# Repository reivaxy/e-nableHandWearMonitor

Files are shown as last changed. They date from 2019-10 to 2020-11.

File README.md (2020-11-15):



# e-nableHandWearMonitor

This device is intended to track the time spans during which an E-nable device is worn by its owner.

## How does it work?

It uses a sensor to detect that the device is worn. Two types of sensors are supported: either a pair of metallic contacts that should be in contact with the skin when the device is worn, or an infrared sensor, that does not need any contact with the skin, which avoids the risk of allergies.

The device has two modes: "recording" and "charging".

In "recording mode" which is as long as the battery lasts, and not plugged into an usb charger, the Esp8266 wakes up at a period that can be set and saved in permanent memory (default is every 5 seconds), checks the presence sensor, and compares its state to the previous time it was checked.

If there is a difference, and for the third time in a row, it records the date and time in a file, in the Esp flash memory, saves the new state, and goes back to deep sleep until it automatically wakes up again.

The "third time in a row" condition insures to not record transient changes that may be due to handling the device while strapping it on, or whatever.

If there is no difference, it just goes back to deep sleep without recording anything.

This allows to save battery life (from 1 to 3 weeks depending on model).

In "charging mode", which is when an usb charger is plugged in, it keeps doing the check but every 2 seconds, won't record any changes, and won't sleep.

Instead it opens up a wifi access point, and  the blue led blinks every 2 seconds to indicate the wifi is activated. When the device has not been set up (or as been reset to factory defaults), the default wifi network SSID is "HandMonitor", and password is the same.

**IMPORTANT: The password should be modified while setting up the device**.

By connecting your phone to this network, you can access the module pages at http://192.168.4.1.

If some settings were already saved at least once, the home page will be displayed.

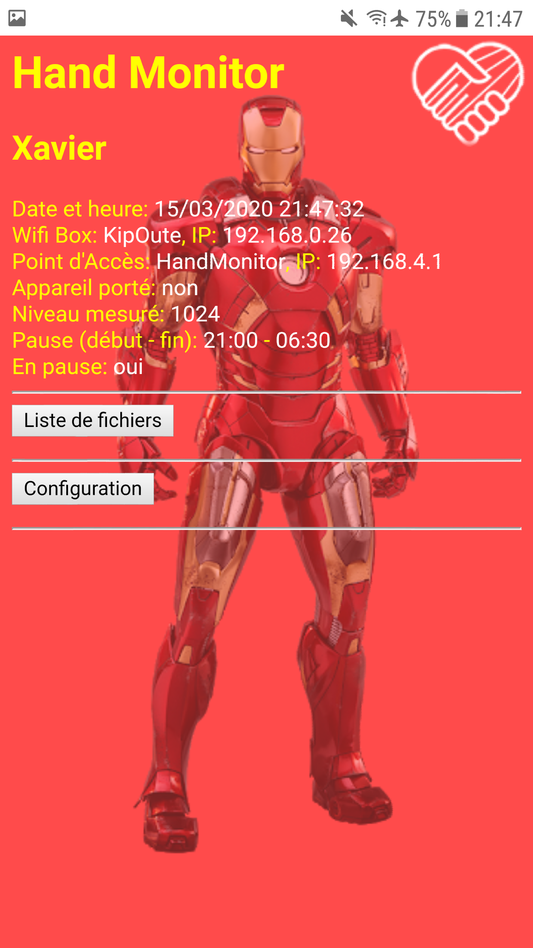
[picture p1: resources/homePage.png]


If the device has never been set up, the settings page will be displayed. 

## The settings page

Here is what the setup settings looks like with a custom skin (more on that later):

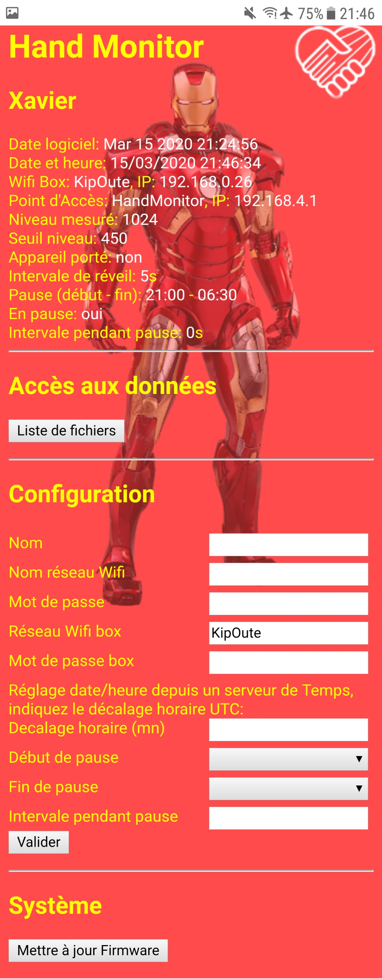
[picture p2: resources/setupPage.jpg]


You should provide a name for the device, for instance its owner first name.

You can change the default ssid/pwd **(please change at least the password)** for the access point wifi network, and, optionally, provide your home wifi ssid and pwd. These are stored locally in the device memory, and never sent anywhere.

Providing your home wifi connection information will allow to automatically setup the date and time in the device, and will allow you to download the data files listing each period the E-nable hand was worn to your computer, and upload file to customize the apparence.

If you don't provide your home wifi connection information you will be able to setup the time manually (work in progress), and download the data files to your computer or phone.

The setup page also displays an "Update firmware" button. When you click on it the device will toggle to OTA (Over the Air) mode, and wait for a new firmware to be uploaded. The blue led will blink twice per second in this mode.

You can then use an android app like "ESP8266 Loader" to upload the new binary from your phone connected to its wifi network, using the device default IP 192.168.4.1

If you provided your home wifi connection information, the update can also be made using the device IP on this network.

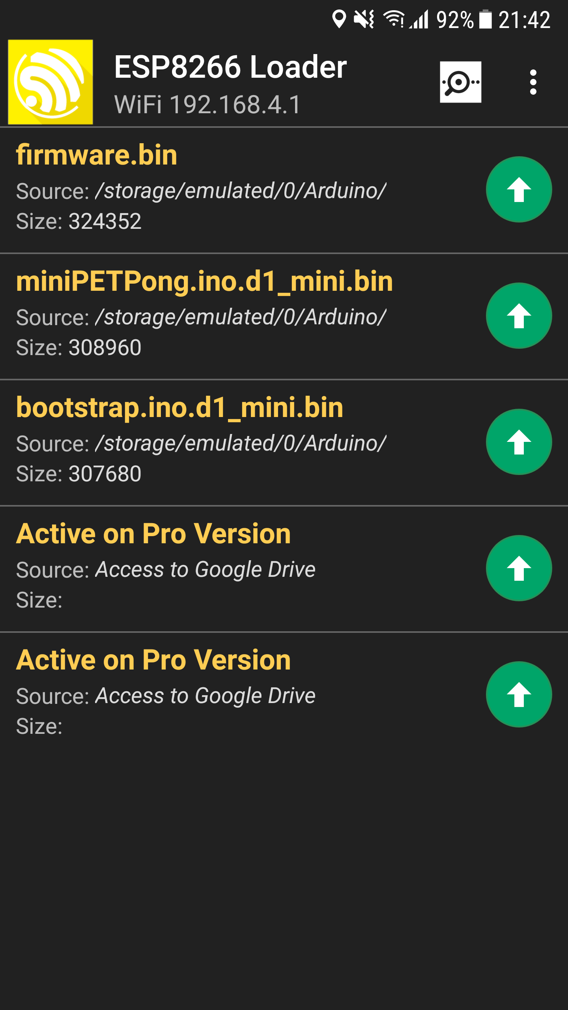
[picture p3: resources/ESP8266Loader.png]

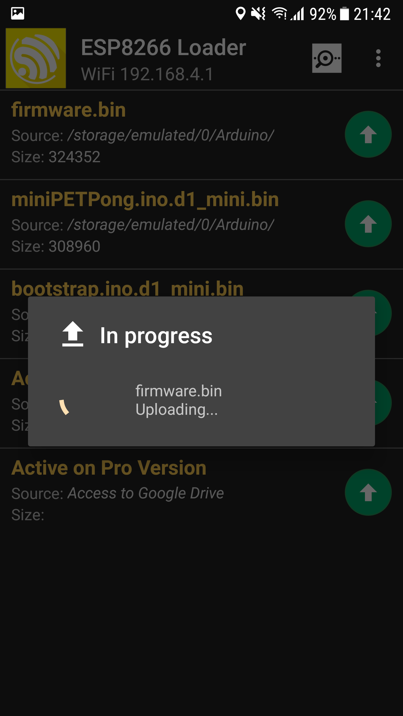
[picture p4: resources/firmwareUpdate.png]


In case a bug breaks the OTA feature in a firmware build, it can still be updated by opening the lid and using the 5 pad solderless connector with a special device to upload a fix through USB connection.

Whatever the upgrade method chosen (OTA or USB), the blue led on the esp will flash frantically while the firmware is uploading.

After the upload is done (and verified) the esp will reboot, updated, and reopen the wifi networks depending on the settings provided.

## Data

The "File list" button will display a page listing all the files in the esp memory. One new file is created each month.

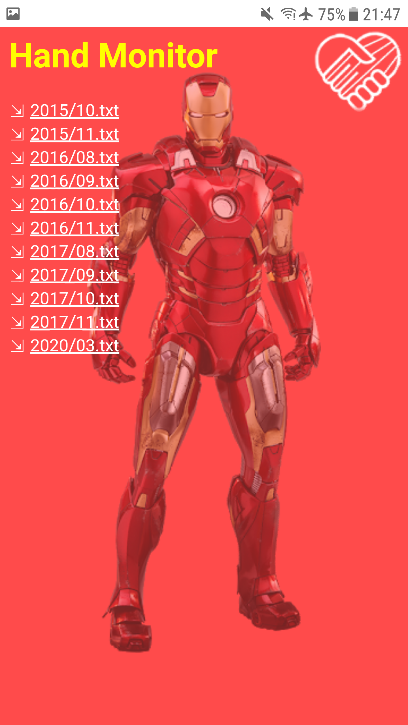
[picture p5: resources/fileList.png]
<kbd></kbd>

You can click on a file name to view its content, or on the arrow in front of it to download it.

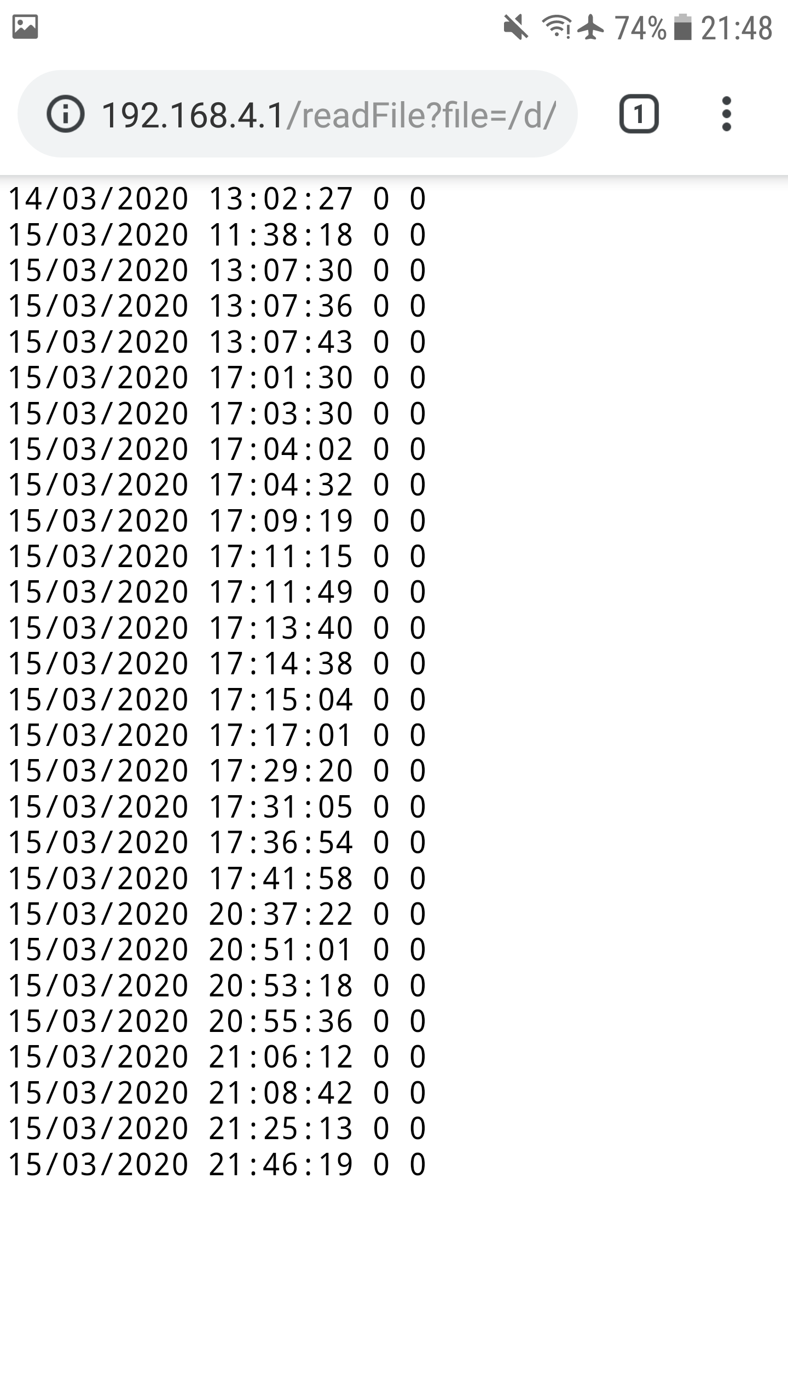
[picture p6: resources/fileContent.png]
<kbd></kbd>

I had no issue recording 15695 lines, in a 223K file (at the time, only the day was saved instead of the full date). 

Each entry is composed of the date, then the hour, minute, second, then the state: 0 means device not worn, 1 means device worn. The actual level of the sensor is then added to the line, to help troubleshoot, if necessary.

A graphical representation of this data can be obtained by dropping one such file [on this webpage](https://reivaxy.github.io/handMonitorDataViz/)
                                                     Data is not uploaded anywhere, and this visualisation tool can be installed locally on any computer without needing a webserver


## "Admin" page

It's a page where some more configuration data as well as "dangerous" features are available: reset the full device (configuration and data files), erase all data files, create test data files...

On this page you can update the wake up period as well as the sensor level threshold that is used to decide if the device is being worn (by detecting skin proximity) or not.

There is also some information on the SPIFFS memory usage, and more will be added if needed.

The "upload file" feature allows you to change the look of the pages if you upload a "custom.css" file. You can also upload images referenced in the css file. Check out the data/w directory for an example featuring an ironman skin.

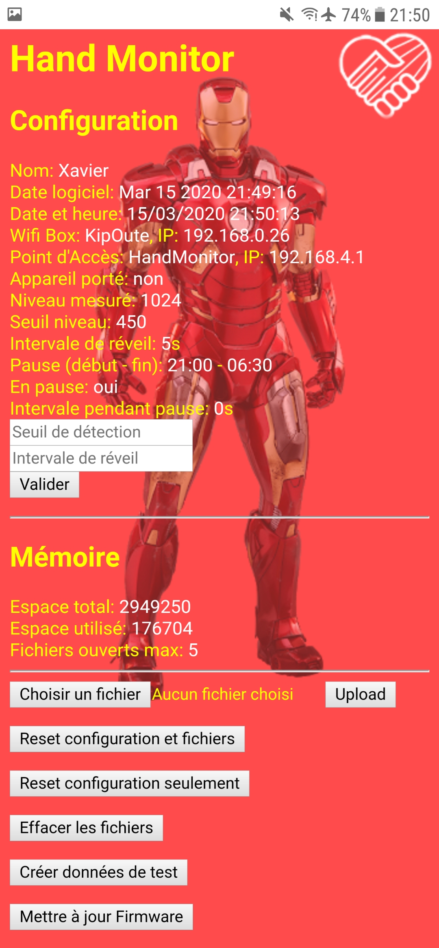
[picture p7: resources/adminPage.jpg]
<kbd></kbd>

## The 1000 mAh version

The prototype shown was built using a 1000mAh battery, which provides an autonomy of more than two weeks.

It is not using the definitive PCB, some wires will be removed, some layout improved to ease assembly.

Here are pictures of this device in its 3D printed case with a slide-in lid:

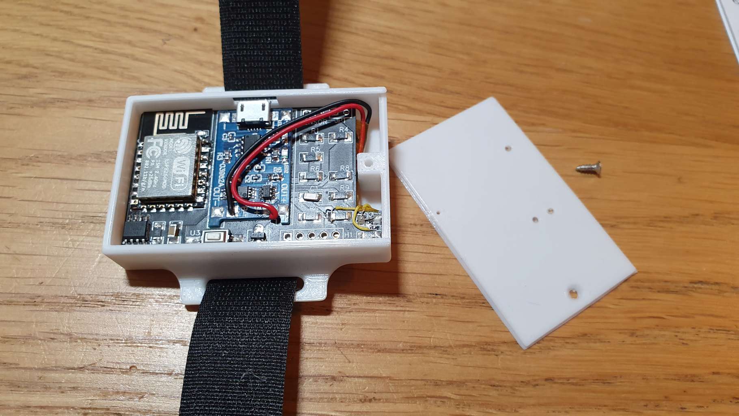
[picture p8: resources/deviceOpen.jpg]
<kbd></kbd>

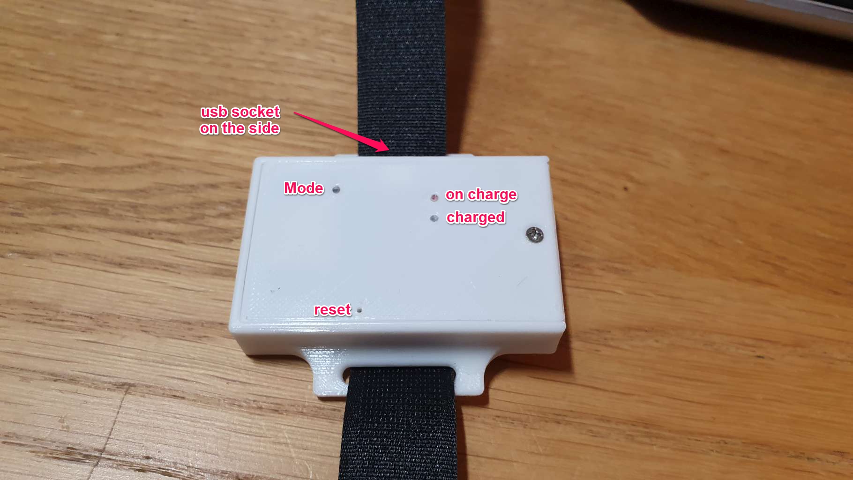
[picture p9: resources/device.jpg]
<kbd></kbd>

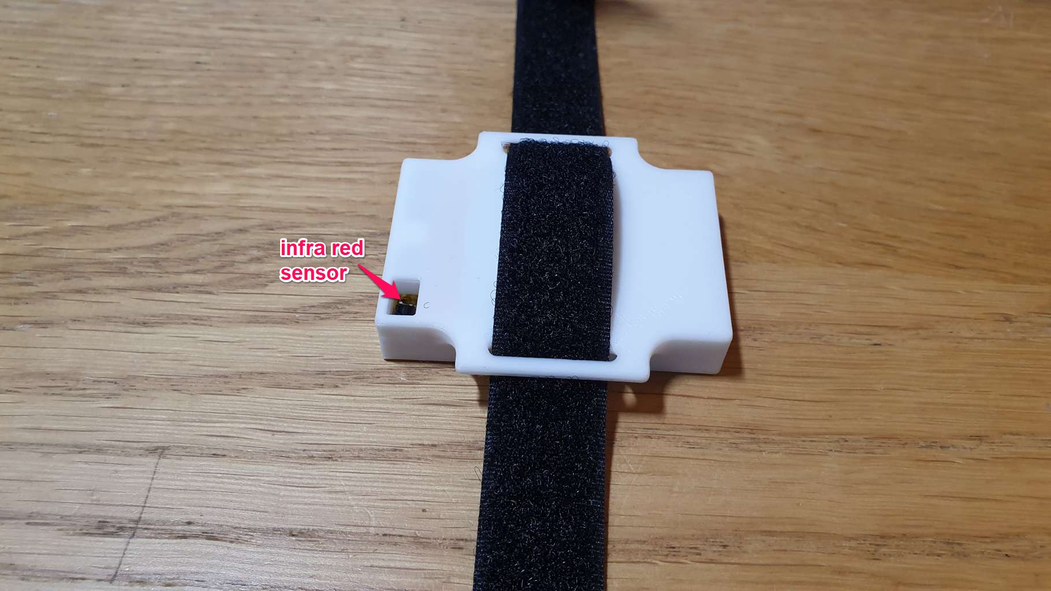
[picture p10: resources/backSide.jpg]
<kbd></kbd>

Solderless connections available on the PCB allow to monitor the serial port for debug messages, as well as flash a new release of the firmware in case OTA feature is broken.

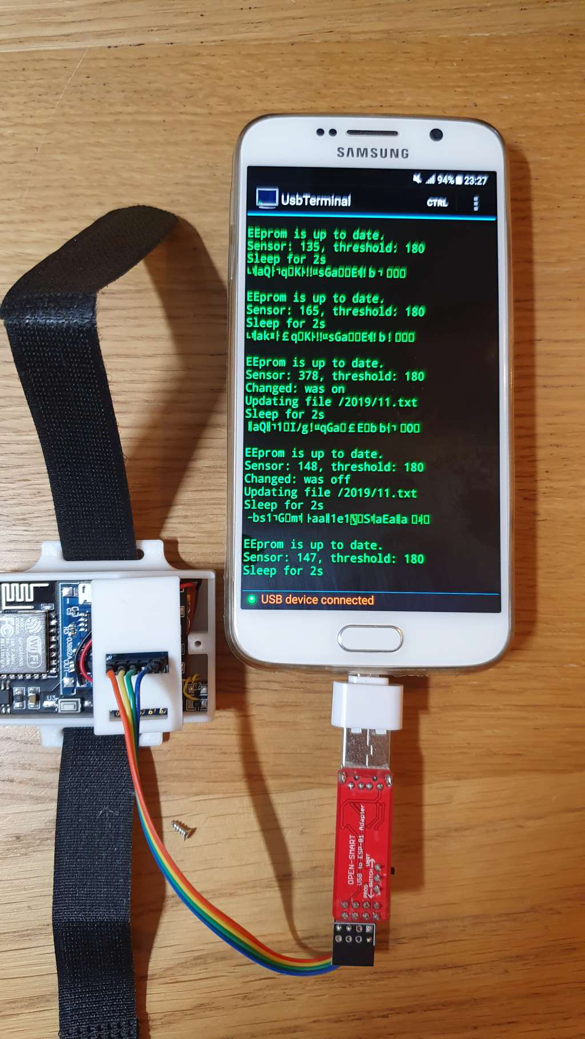
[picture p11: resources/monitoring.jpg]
<kbd></kbd>

Using a custom tool that clips in the lid rails:

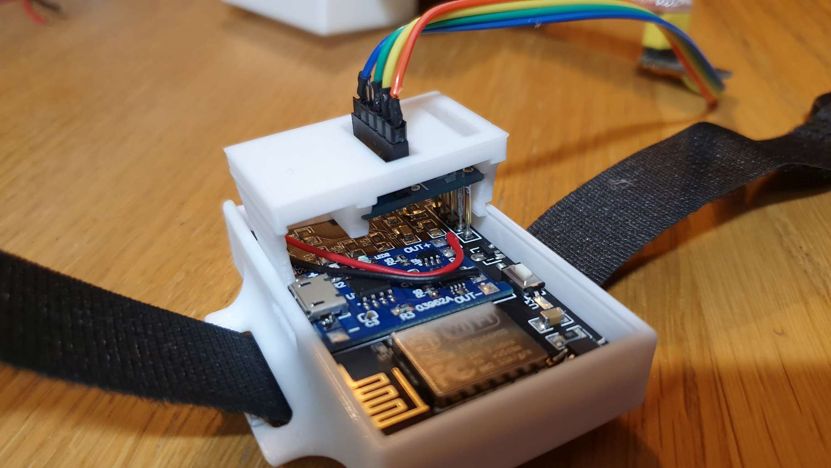
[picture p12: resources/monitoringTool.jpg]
<kbd></kbd>

The PCB is very thin to minimize weight and volume. This prototype PCB has a faulty IR sensor package layout and incorrect battery connection to charger, fixed for next version.

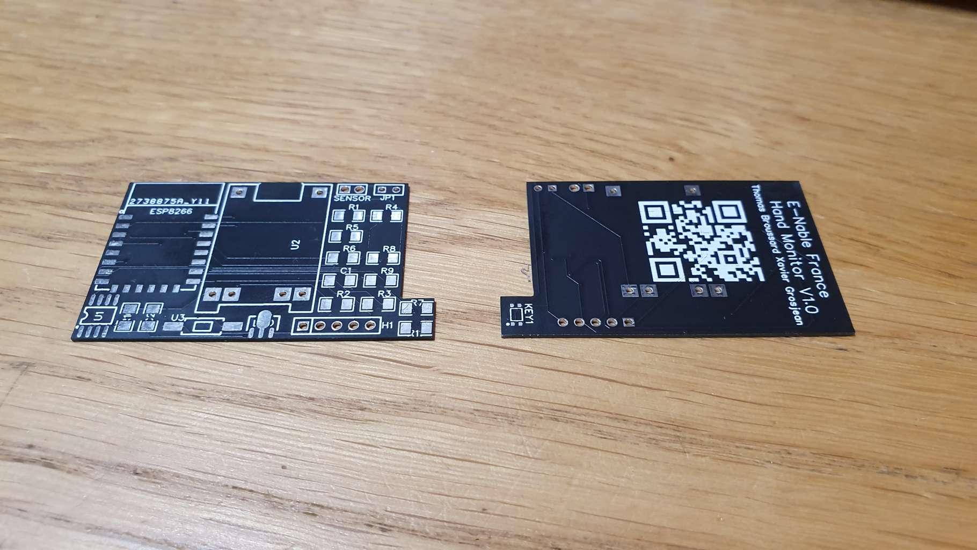
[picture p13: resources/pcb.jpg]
<kbd></kbd>

 ## The 300 mAh version

 The model above is a bit too big and too heavy for young kids, so I built another one, much smaller, using a 300mAh battery, which still gives it a little over one week of autonomy.

 This is the first prototype.

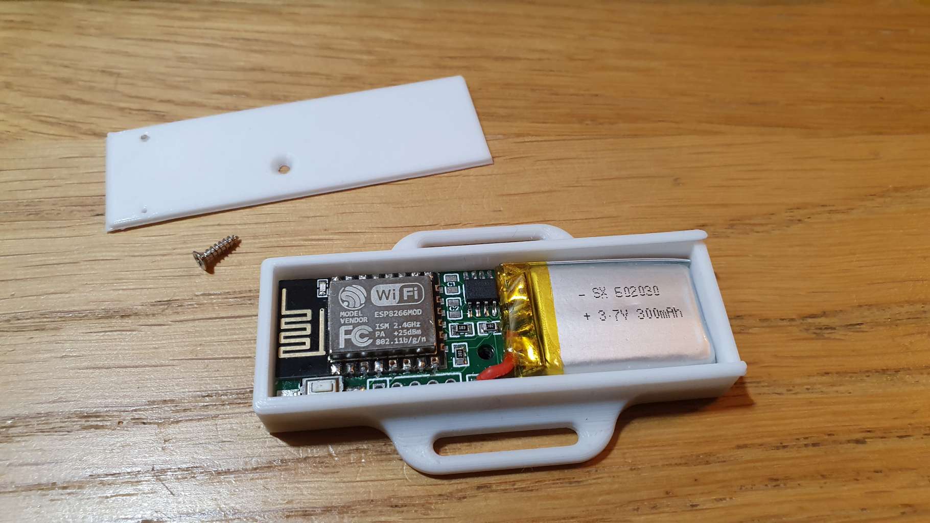
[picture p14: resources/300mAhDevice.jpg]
<kbd></kbd>

Since its shape is a bit long, it is not convenient for a small hand (printed at 100% scale), which is why I designed this third layout:

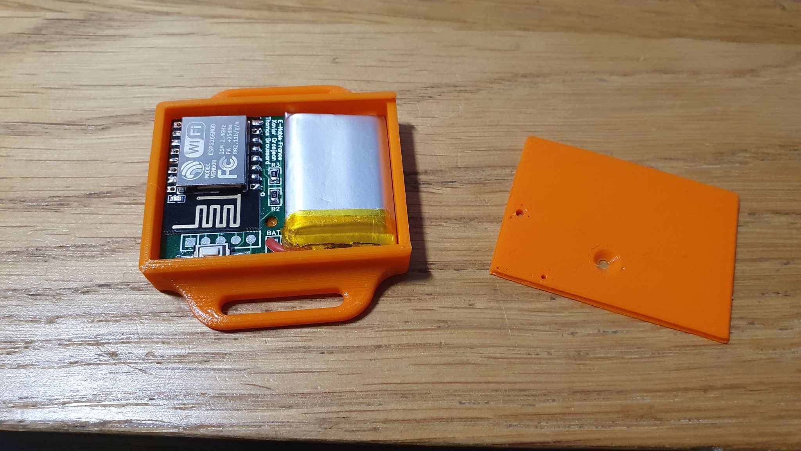
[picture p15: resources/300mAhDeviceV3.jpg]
<kbd></kbd>

All PCB's are (or will be made) available in the repository, as well as 3D designs to 3D-print the cases and the clip-on device to access serial connection for debuging or flashing firmware.

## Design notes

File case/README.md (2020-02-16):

# 3D files for case, lid and clip-on connector

Here are the source files to 3D print the cases for the handmonitor.

The dimensions need to be accurate for the PCB and battery to fit tightly, and the PCB should be 0.8mm thick.

The V1, aka "1000mAh", version is available in 1 layout.

The 300mAh version is available in 2 layouts:

- V2: long case

- V3: squarrish case  NOT READY FOR REAL PCB YET, just a POC

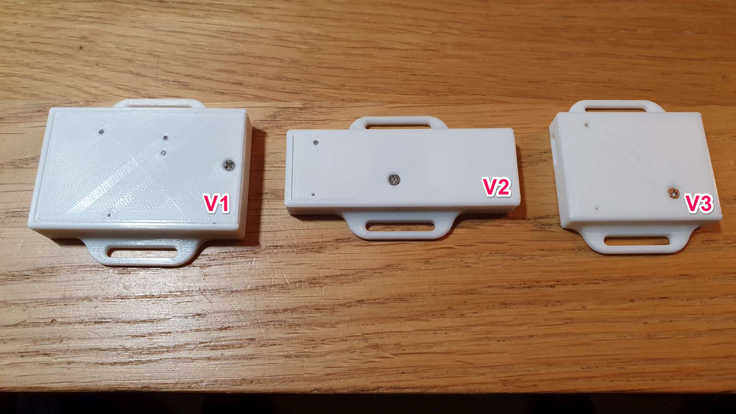
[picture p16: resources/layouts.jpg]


The 3 small holes for the mode and charging LEDs are intended to be filled with a small bit of  ⌀1mm plastic optical fiber.

# Black well for better results
Ideally, the IR sensor well should be printed in black, to improve sensor levels differenciation between "worn" and "not worn" states.

Using the same elctronic device in the two cases below, the level on the sensor when the device was not worn was twice as high with the black well than with the white well.

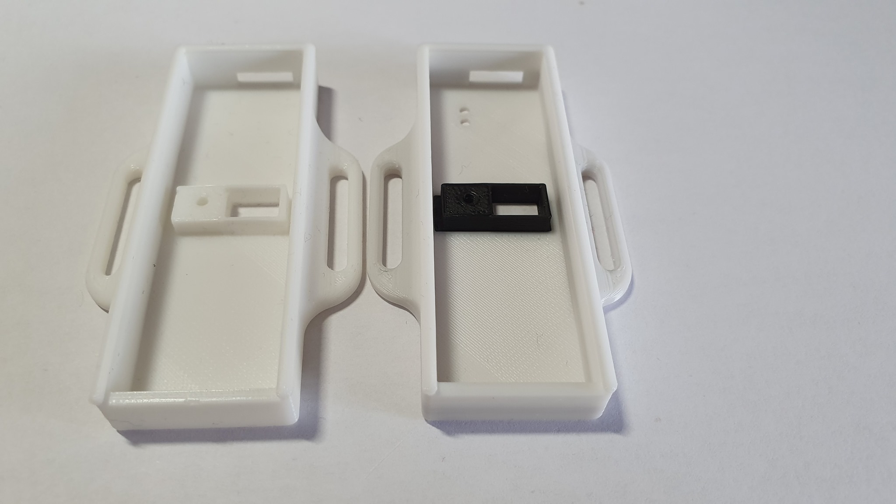
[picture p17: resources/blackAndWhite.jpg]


When printing a black well is not possible then its inside walls should be painted with black acrylic paint, for instance.

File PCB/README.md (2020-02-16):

# Fabrication files.

If you are going to use the provided STLs to 3D print the case, make sure to order a 0.8mm pcb

Several different PCBs were actually made for each version (1000mAh and 300mAh), but the schematic is identical for each.



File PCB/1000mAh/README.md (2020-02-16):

# Fabrication files for 1000mAh version PCB

If you are going to use the provided STLs to 3D print the case, make sure to order a 0.8mm pcb

V1.0 is buggy due to incorrect IR detector package. It is still in this repo since 5 PCBs were made

V1.1 fixes that, along with some layout change to ease component soldering

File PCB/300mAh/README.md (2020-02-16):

# Fabrication files for 300mAh version PCB

If you are going to use the provided STLs to 3D print the case, make sure to order a 0.8mm pcb

## V2 is the long version.

V2.0 is not optimal for ESP led position, that might be hidden by scratch band when using provided case STL. 

V2.1 fixes that by rotating ESP

## V3 is the squarrish version.
No issue reported so far.

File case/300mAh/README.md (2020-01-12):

If possible, the well (hole for the IR sensor) should be printed in black in order to less reflect the IR light to the sensor.

It helps setting the threshold to a value that ensures no detection error.

The hook should be printed in ABS for more elasticity. It's tight, and PLA breaks too easily.

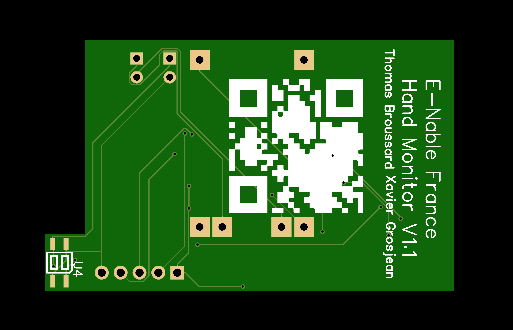
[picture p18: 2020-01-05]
PCB/1000mAh/V1.1_BOTTOM.png

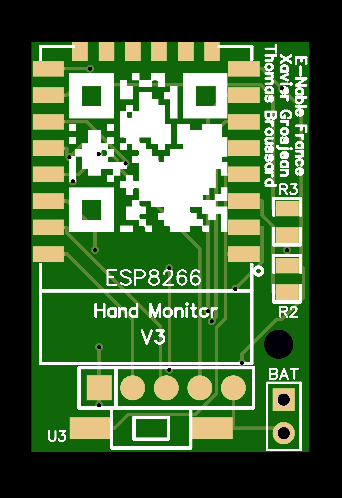
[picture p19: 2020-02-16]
PCB/300mAh/V3/V3.0_TOP.png

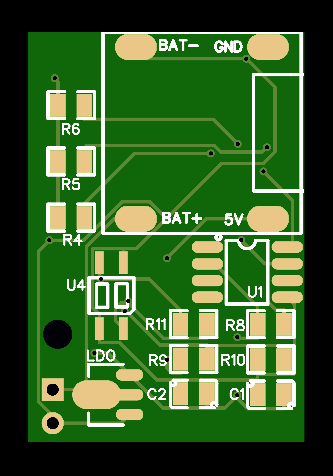
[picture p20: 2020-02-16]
PCB/300mAh/V3/V3.0_BOTTOM.png

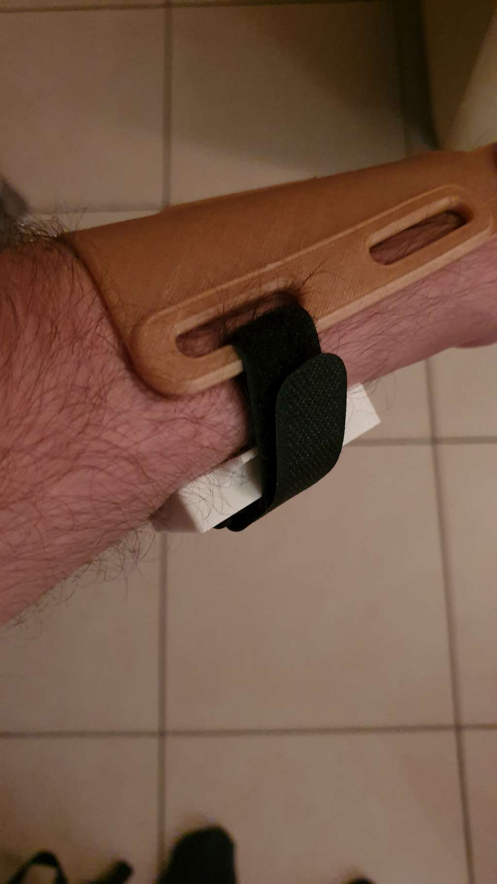
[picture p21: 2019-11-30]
resources/wearing.jpg

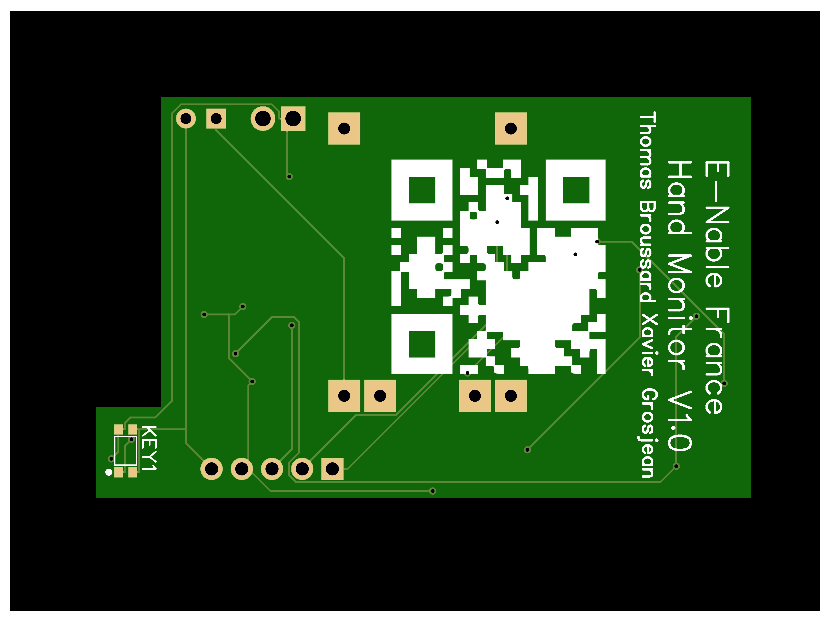
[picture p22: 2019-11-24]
PCB/1000mAh/V1.0_BOTTOM.png

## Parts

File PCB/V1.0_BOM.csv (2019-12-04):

ID | Name | Designator | Footprint | Quantity | Manufacturer Part | Manufacturer | Supplier | Supplier Part | LCSC Assembly | Prix unitaire approximatif | Prix total
1 | ESP8266-12F | ESP8266 | LGA22-2.0-24X16MM | 1 | ESP8266-12F/ESP-12F |  |  |  |  | 1,30 € | 1,30 €
2 | DS3231MZ+ | U1 | SOIC-8_150MIL | 1 | DS3231MZ+ | MAXIM | LCSC | C107410 | Yes | 2,00 € | 2,00 €
3 | Tactile switch SMD 2 Pin | U3 | TACTILE SWITCH SMD 2PIN | 1 |  |  |  |  |  | 0,01 € | 0,01 €
4 | 100n | C1 | 1206 | 1 |  |  |  |  |  | 0,01 € | 0,01 €
5 | 1u | C2 | 1206 | 1 |  |  |  |  |  | 0,01 € | 0,01 €
6 | TP4056 | U2 | 03962A | 1 |  |  |  |  |  | 0,30 € | 0,30 €
7 | Header-Male-2.54_1x5 | H1 | DIP-1X5P-2.54MM-M | 1 | 210S-1*5P L=11.6MMGold-plated black | Ckmtw | LCSC | C124379 |  |  | 0,00 €
8 | MCP1702T-3302E/MB | LDO | SOT-89(SOT-89-3) | 1 | MCP1702T-3302E/MB | MICROCHIP | LCSC | C88418 | Yes | 1,00 € | 1,00 €
9 | ITR8307/S18/TR8(B) | U4 | ITR20510/TR8 | 1 | ITR8307/S18/TR8(B) | EVERLIGHT | LCSC | C115037 |  | 0,50 € | 0,50 €
10 | 10k | R2,R4,R5,R6,R8 | 1206 | 5 |  |  |  |  |  | 0,01 € | 0,03 €
11 | 1k | R3 | 1206 | 1 |  |  |  |  |  | 0,01 € | 0,01 €
12 | 1M | R1 | 1206 | 1 |  |  |  |  |  | 0,01 € | 0,01 €
13 | 180k | R9 | 1206 | 1 |  |  |  |  |  | 0,01 € | 0,01 €
14 | 100k | R10 | 1206 | 1 |  |  |  |  |  | 0,01 € | 0,01 €
15 | 220 | R7 | 1206 | 1 |  |  |  |  |  | 0,01 € | 0,01 €
16 | 33k | R11 | 1206 | 1 |  |  |  |  |  | 0,01 € | 0,01 €
17 | Header-Male-2.54_1x2 | SENSOR | HDR-2X1/2.54 | 1 | 826629-2 | TE Connectivity | LCSC | C86471
18 | 2 Pin Header | BAT | HDR1X2 | 1
 | batterie lipo 1000mAh |  |  | 1 |  |  |  |  |  | 3,00 € | 3,00 €
 | PCB |  |  | 1 |  |  |  |  |  | 1,3 | 1,3
 |  |  |  |  |  |  |  |  |  | Total | 9,49 €

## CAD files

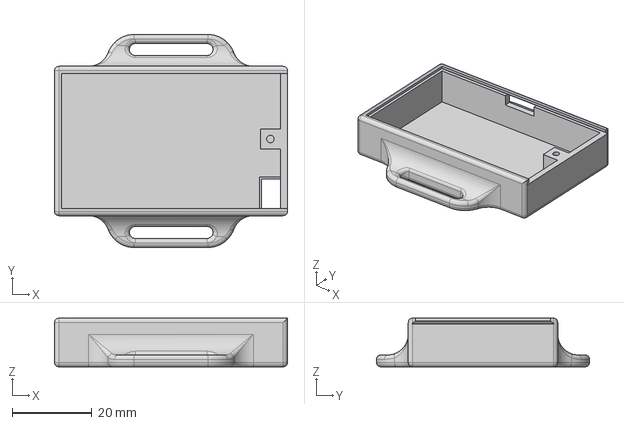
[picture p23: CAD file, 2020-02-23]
case/1000mAh/CaseOnStraps.step
58.6 x 53.6 x 12.2 mm

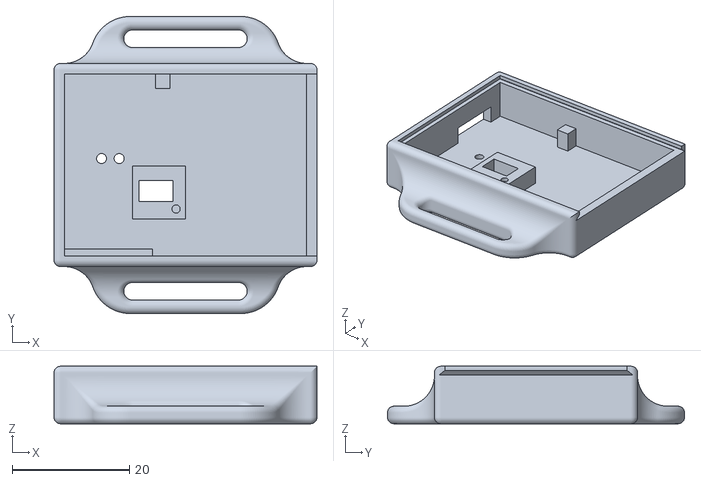
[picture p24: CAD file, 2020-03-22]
case/300mAh/V3/CaseOnStraps.stl
44.8 x 50.6 x 9.80

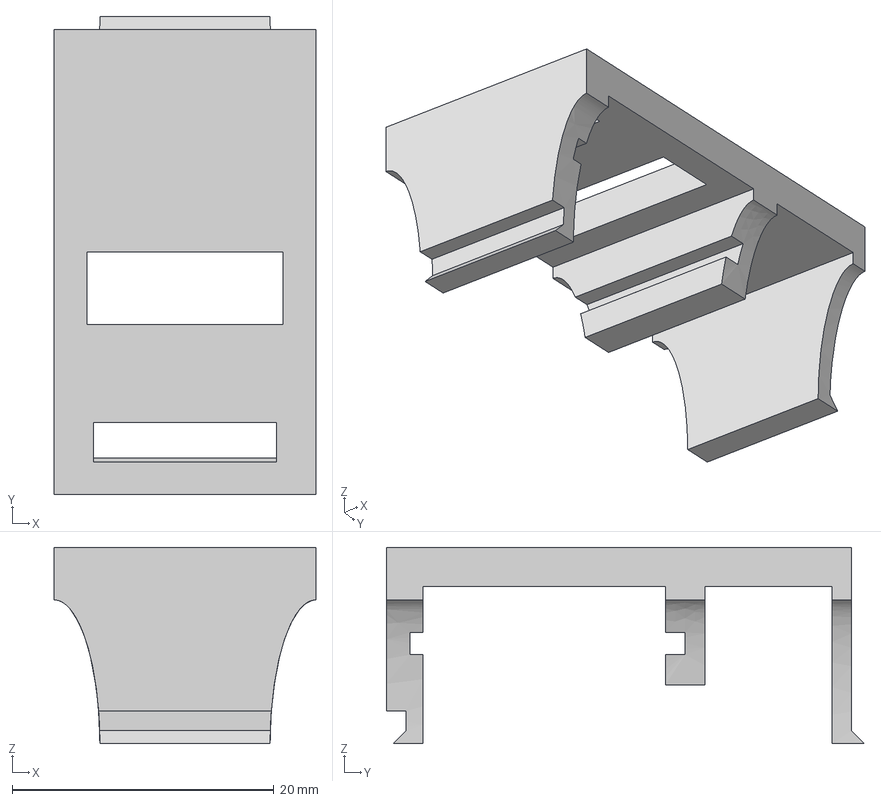
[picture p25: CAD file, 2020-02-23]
case/1000mAh/Hook.step
20.0 x 36.5 x 15.0 mm

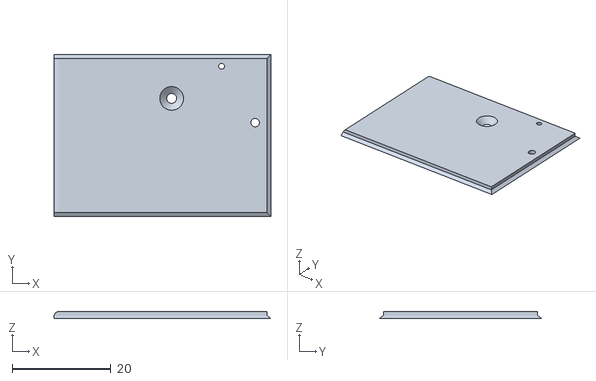
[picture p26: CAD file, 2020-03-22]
case/300mAh/V3/Lid.stl
43.9 x 32.8 x 1.40

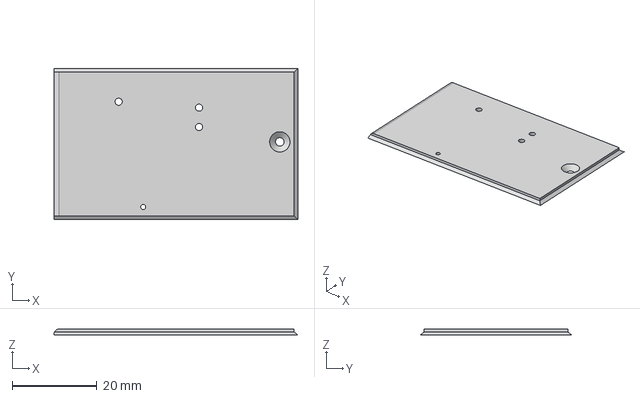
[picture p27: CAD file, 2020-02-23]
case/1000mAh/Lid.step
57.7 x 35.8 x 1.40 mm

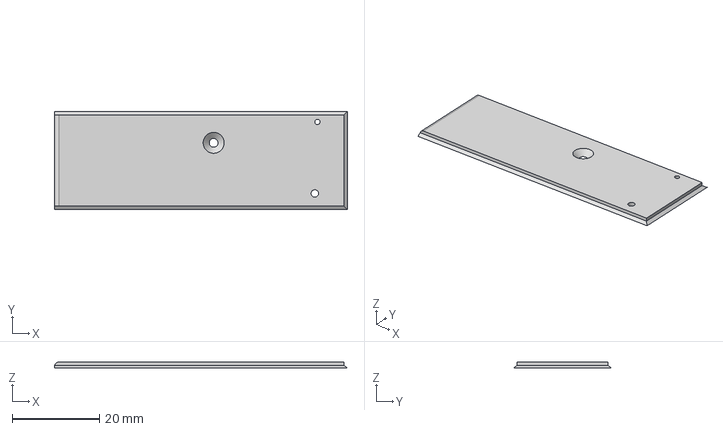
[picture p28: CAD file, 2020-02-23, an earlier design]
case/300mAh/V2/Lid.step
67.2 x 22.5 x 1.40 mm

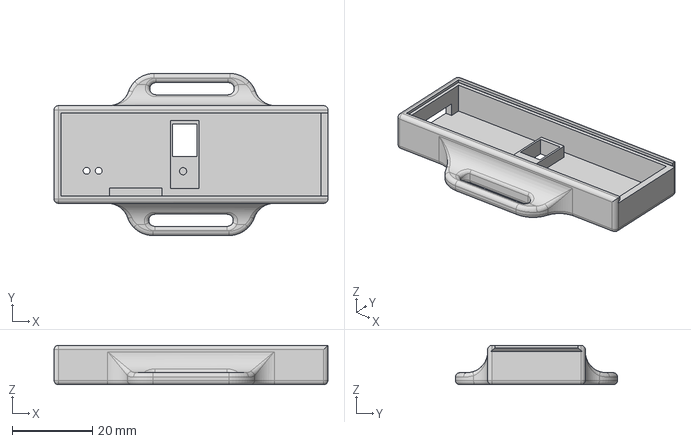
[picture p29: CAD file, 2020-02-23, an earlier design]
case/300mAh/V2/CaseOnStraps.step
68.1 x 40.3 x 9.80 mm

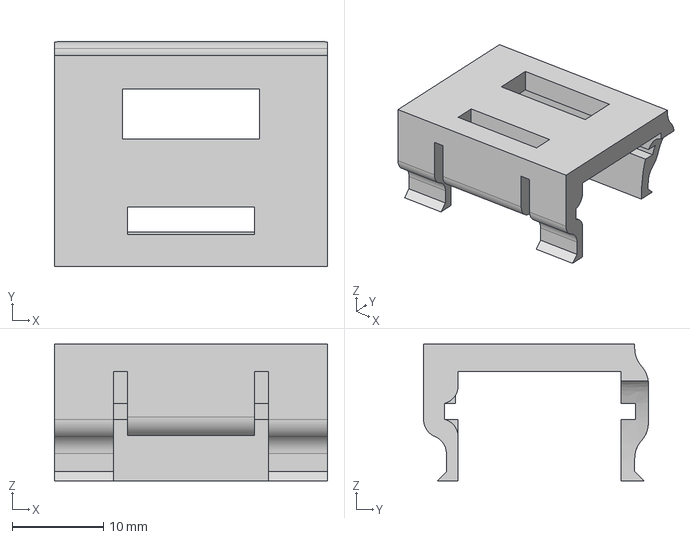
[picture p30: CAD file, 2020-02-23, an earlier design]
case/300mAh/V2/Hook.step
30.0 x 24.7 x 15.0 mm

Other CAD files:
case/1000mAh/CaseOnStraps.stl
case/1000mAh/Hook.stl
case/1000mAh/Lid.stl
case/300mAh/V2/CaseOnStraps.stl
case/300mAh/V2/Hook.stl
case/300mAh/V2/Lid.stl

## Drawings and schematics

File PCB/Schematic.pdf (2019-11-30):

## Notice: VCC=3.3v

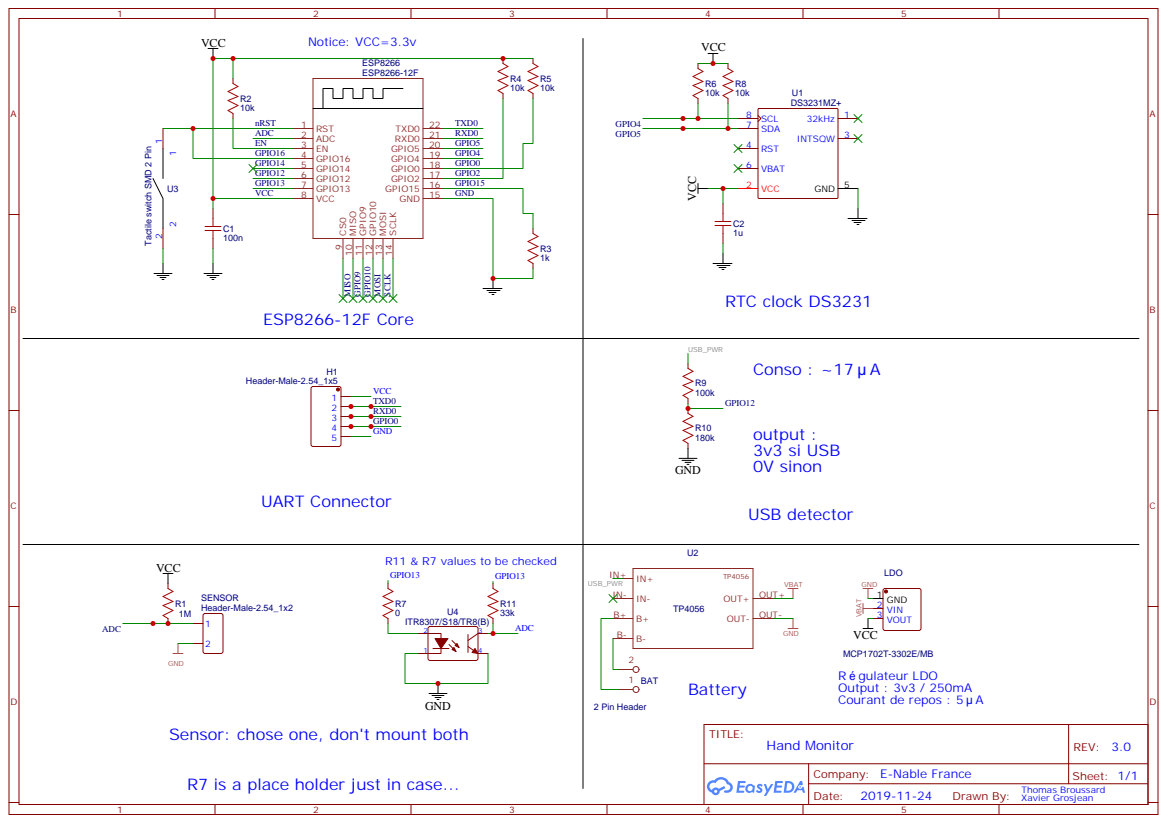
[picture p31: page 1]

Tactile switch SMD 2 Pin

R11 & R7 values to be checked

Sensor: chose one, don't mount both

R7 is a place holder just in case...

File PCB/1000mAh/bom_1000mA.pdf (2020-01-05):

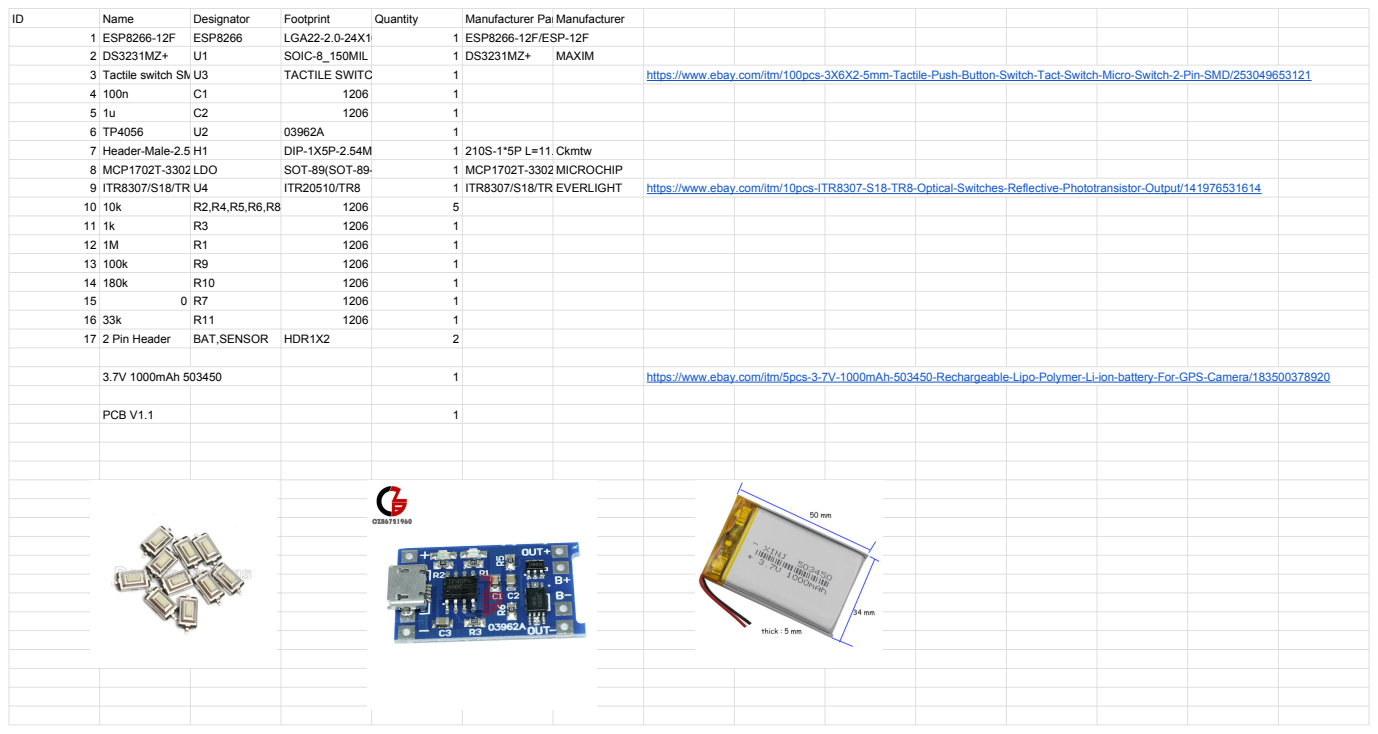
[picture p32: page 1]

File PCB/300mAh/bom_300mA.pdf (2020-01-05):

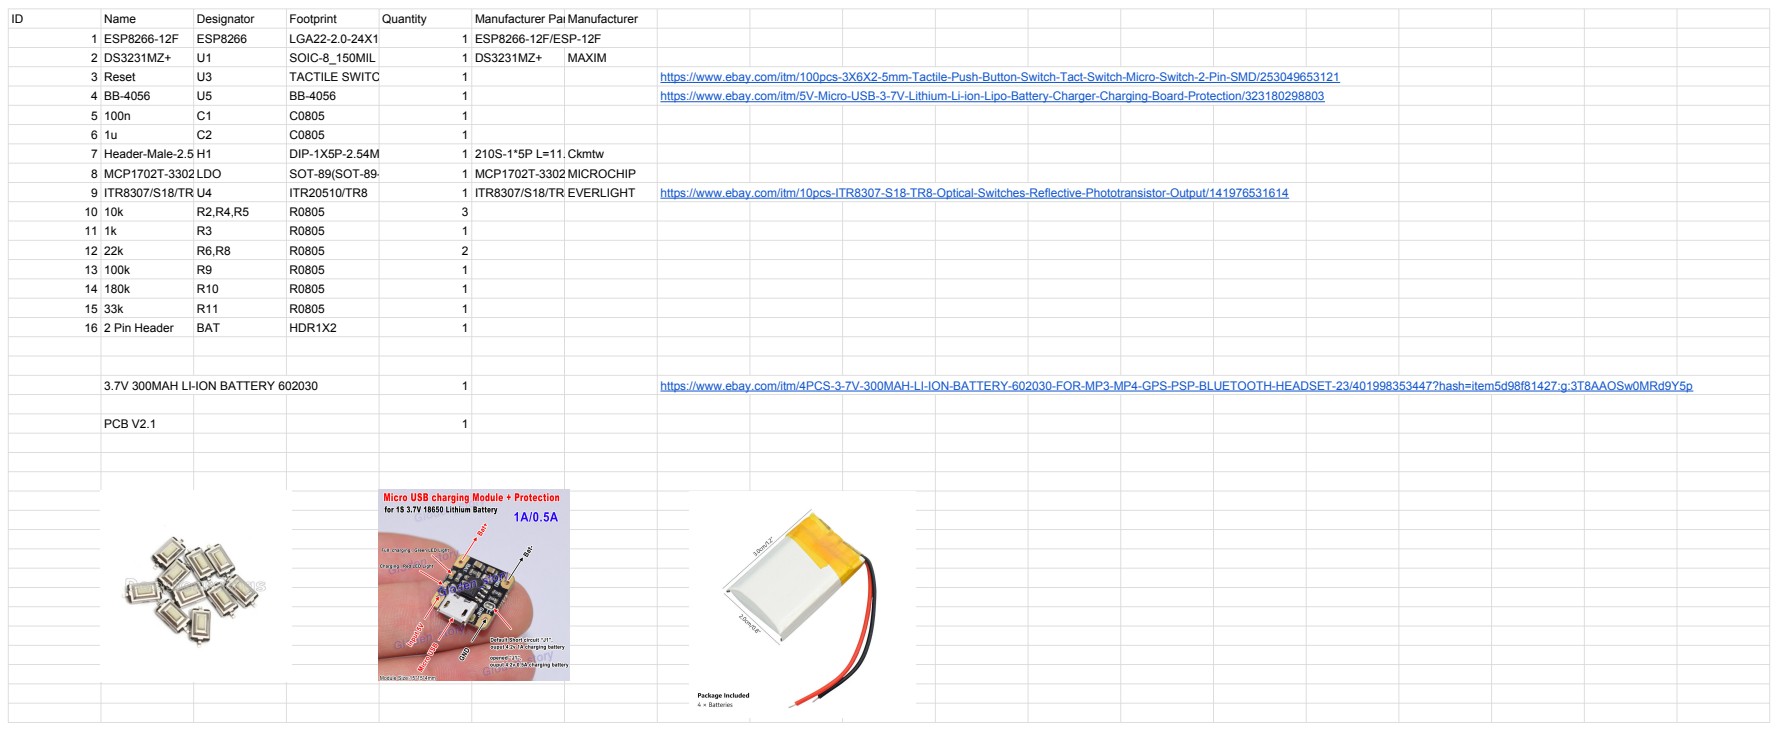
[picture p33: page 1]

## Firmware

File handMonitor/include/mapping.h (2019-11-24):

/* 
 *  =============================================================================================================================================
 *  Project : Hand Monitoring e-Nable France
 *  Author  : Xavier Grosjean & Thomas Broussard
 * 
 *  ---------------------------------------------------------------------------------------------------------------------------------------------
 *  Description : 
 * 
 * =============================================================================================================================================
 */

#ifndef __MAPPING_H__
#define __MAPPING_H__

/* 
* ====================================================================================
*                                  I/O Mapping
* ====================================================================================
*/

/** RTC Clock */
#define PIN_RTC_SCL 4
#define PIN_RTC_SDA 5

/** Sensor */
#define PIN_SENSOR  A0

/** Charger detection */
#define PIN_POWER_DETECT 12

/** Infra red emitter */
#define PIN_IR_EMITTER 13

#endif

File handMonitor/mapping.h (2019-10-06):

/* 
 *  =============================================================================================================================================
 *  Project : Hand Monitoring e-Nable France
 *  Author  : Reivaxy & Thomas Broussard
 * 
 *  ---------------------------------------------------------------------------------------------------------------------------------------------
 *  Description : 
 * 
 * =============================================================================================================================================
 */

#ifndef __MAPPING_H__
#define __MAPPING_H__

/* 
* ====================================================================================
*                                  I/O Mapping
* ====================================================================================
*/

/** RTC Clock */
#define PIN_RTC_SCL 4
#define PIN_RTC_SDA 5
#define PIN_RTC_VCC 16

/** Sensor */
#define PIN_SENSOR  A0

/** Charger detection */
#define PIN_POWER_DETECT 12


/* 
* ====================================================================================
*                                  Debugging
* ====================================================================================
*/

// remove '//' to enable debug mode
//#define __DEBUG

#ifdef __DEBUG
   #define DebugPrintln(x)  Serial.println(x)
   #define DebugPrint(x)    Serial.print(x)
#else
   #define DebugPrintln(x)
   #define DebugPrint(x)  
#endif

#ifdef __DEBUG
   #define DebugBegin()  Serial.begin(9600)
#else
   #define DebugBegin()
#endif


#endif

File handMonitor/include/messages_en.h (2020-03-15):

/* 
 *  =============================================================================================================================================
 *  Project : Hand Monitoring e-Nable France
 *  Author  : Xavier Grosjean & Thomas Broussard
 * 
 *  ---------------------------------------------------------------------------------------------------------------------------------------------
 *  Description : french messages for embedded server web pages
 * 
 * =============================================================================================================================================
 */

#pragma once

#define MSG_TITLE "Hand Monitor"
#define MSG_INIT_AP_SSID "Wifi network name"
#define MSG_INIT_AP_PWD "Password"
#define MSG_INIT_HOME_SSID "Home Wifi network name"
#define MSG_INIT_HOME_PWD "Home Wifi passord"
#define MSG_INIT_NTP_HOST "NTP server"
#define MSG_INIT_WEBSITE "Web Site"
#define MSG_INIT_API_KEY "Key"
#define MSG_START_OTA "Firmware update"
#define MSG_WAITING_OTA "Ready for OTA on IP %s"
#define MSG_CONFIG_SAVED "Data saved"
#define MSG_RESET "Reset"
#define MSG_FILE_LIST "File list"
#define MSG_CURRENT_TIME "Date and time"
#define MSG_DATA "Access data"
#define MSG_CONFIG "Configuration"
#define MSG_SYSTEM "System"
#define MSG_BUILD_DATE "Firmware date"
#define MSG_INIT_SENSOR_THRESHOLD "Sensor threshold"
#define MSG_INIT_REFRESH_INTERVAL "Refresh interval"
#define MSG_INIT_TIME_OFFSET "Time offset (mn)"
#define MSG_TIME_OFFSET "Current date/time fetched from a Time server, provide your timezone UTC time difference:"
#define MSG_MANUAL_TIME_SETTING "Set current date/time manually:"

#define MSG_PAUSE "Pause (start - end)"
#define MSG_INIT_START_PAUSE "Start pause at"
#define MSG_INIT_END_PAUSE "End pause at"
#define MSG_INIT_PAUSE_REFRESH_INTERVAL "Pause refresh interval"
#define MSG_IS_PAUSED "Paused"

#define MSG_INIT_NAME "Name"

#define MSG_DOWNLOAD "Download"
#define MSG_DELETE "Delete"
#define MSG_LEVEL "Current level"
#define MSG_THRESHOLD "Threshold level"
#define MSG_INIT_PAGE "Settings"
#define MSG_HOME_WIFI "Home Wifi"
#define MSG_AP_WIFI "Access Point"
#define MSG_UNDEFINED "Not set"
#define MSG_MEMORY "Memory"
#define MSG_WORN "Device is worn"

#define MSG_RESET_ALL "Reset config & files"
#define MSG_RESET_CONFIG "Reset config only"
#define MSG_ERASE_FILES "Erase all files"
#define MSG_CREATE_FAKE_DATA "Create test data"

#define MSG_MEMORY_SIZE "Total space"
#define MSG_MEMORY_USED "Used space"
#define MSG_MEMORY_MAX_FILES "Max open files"

#define MSG_YES "yes"
#define MSG_NO "no"

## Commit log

2019-10-06 Switched to platformio project structure, added wifi AP on power detection
2019-10-08 Inverted SDL and SDA to match Wire library default. To be validated by Thomas
2019-10-12 Now saves each change on sensor to SPIFFS file, one per month.
2019-10-13 prototype, and some screenshots
2019-10-18 Refactored led handling. Now blinking slowly when wifi network is exposed, rapidly when waiting for OTA, frantically while uploading
2019-11-24 Handling IR sensor
    [V1.0_BOM.csv]
2019-11-30 Added sensor threashold and refresh period to configuration
    [V1.0_BOM.csv]
2019-11-30 Pictures of the 1000 mAh device
2019-11-30 Adding 3D files for case, lid and monitoring tool
    [Case.stl, CaseOnStraps.stl, Hook.stl, Lid.stl]
2019-11-30 Added pcb picture
2019-12-04 Adding gerber files
    [V1.0_BOM.csv]
2019-12-05 moved STLs to subdirectory 1000mAh
    [Case.stl, CaseOnStraps.stl, Hook.stl, Lid.stl]
2019-12-27 Pivoted ESP 180° for better led position
2020-01-05 Adding BOM and PCB snapshots
2020-01-11 3D files for 300mAh device case
    [CaseOnStraps.stl, Lid.stl]
2020-01-12 Adding hook
    [Hook.stl]
2020-02-15 Home page simplification, once device was initialized. Loading dynamic data using Json Updated README Added css
    [CaseOnStraps.stl]
2020-02-16 Fixed README typos Reorganized PCB directory
2020-02-16 Some directory reorganization README improvements
    [Case.stl, CaseOnStraps.stl, Hook.stl, Lid.stl]
2020-02-23 Adding step files for two validated cases
    [CaseOnStraps.step, Hook.step, Lid.step]
2020-03-21 adding ArduinoJson lib
2020-03-21 Need version 5 of ArduinoJson lib
2020-03-22 Fixed pause period lost when saving other parameters
    [CaseOnStraps.stl, Lid.stl]
